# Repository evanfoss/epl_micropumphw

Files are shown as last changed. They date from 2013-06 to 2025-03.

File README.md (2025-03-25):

# EPL Micropump Hardware

This project was the hardware to be accompanied by the <a href="https://github.com/EPL-Engineering/epl_impup-fw">EPL Micropump Firmware</a> which is <a href="https://github.com/evanfoss/epl_micropumpfw">mirrored here</a>. The pair of projects is a wearable intracochlear drug delivery pump.

WARNING: This device is not for use on humans. It was experimental and not intended for actual medical use.

## History
1. The initial version was done by Ishmael S. Wagner it was built in a large inclosure from Bud Industries.
2. The 2nd version was built based on the original by Evan Foss & Ishmael S. Wagner. It fit in an enclosure 3D printed and covered in kapton tape by Draper Lab.
3. The 3rd version was a revision on the 2nd by Evan Foss & Ishmael S. Wagner. The board was produced but the project was canceled by the PI.

### Acknowledgements

I would like to thank Dianna Sands for the suggestion of using a balloon as the reservior.

## Specifications

* Small size
* Low weight
* Long battery life (+1 Week)
* Rechargable batteries
* Consisten flow rate and pressure over whole operating life
* Status indicator LEDs
* Pushbutton to prime fluid lines
* 2 Position switch to set operating mode (optional)
* Potentiometer to set flow rate (optional)

# Development

## Toolchain

The development toolchain was as follows:

|Tool Name                                                                                   | License           | Function
|:---------------                                                                            | :-------------    | :-----------------
|<a href="https://github.com/lepton-eda/lepton-eda">lepton-eda</a>                           | Open Source       | EDA (Electronic Design Automation) suite lepton-eda a fork of gEDA
|<a href="http://repo.hu/projects/pcb-rnd/">pcb-rnd</a>                                      | Open Source       | CAD (Computer Aided Design) tool for PCB (Printed Circuit Board) layout gEDA/PCB
|<a href="https://gerbv.github.io/">gerbv</a>                                                | Open Source       | Gerber viewer
|<a href="https://www.gnu.org/software/make/">GNU/Make</a>                                   | Open Source       | Toolchain automation

Note: The CAD drawings for the 3D printed case are lost to history is the name of the software used to draft them.

## Circuit Design

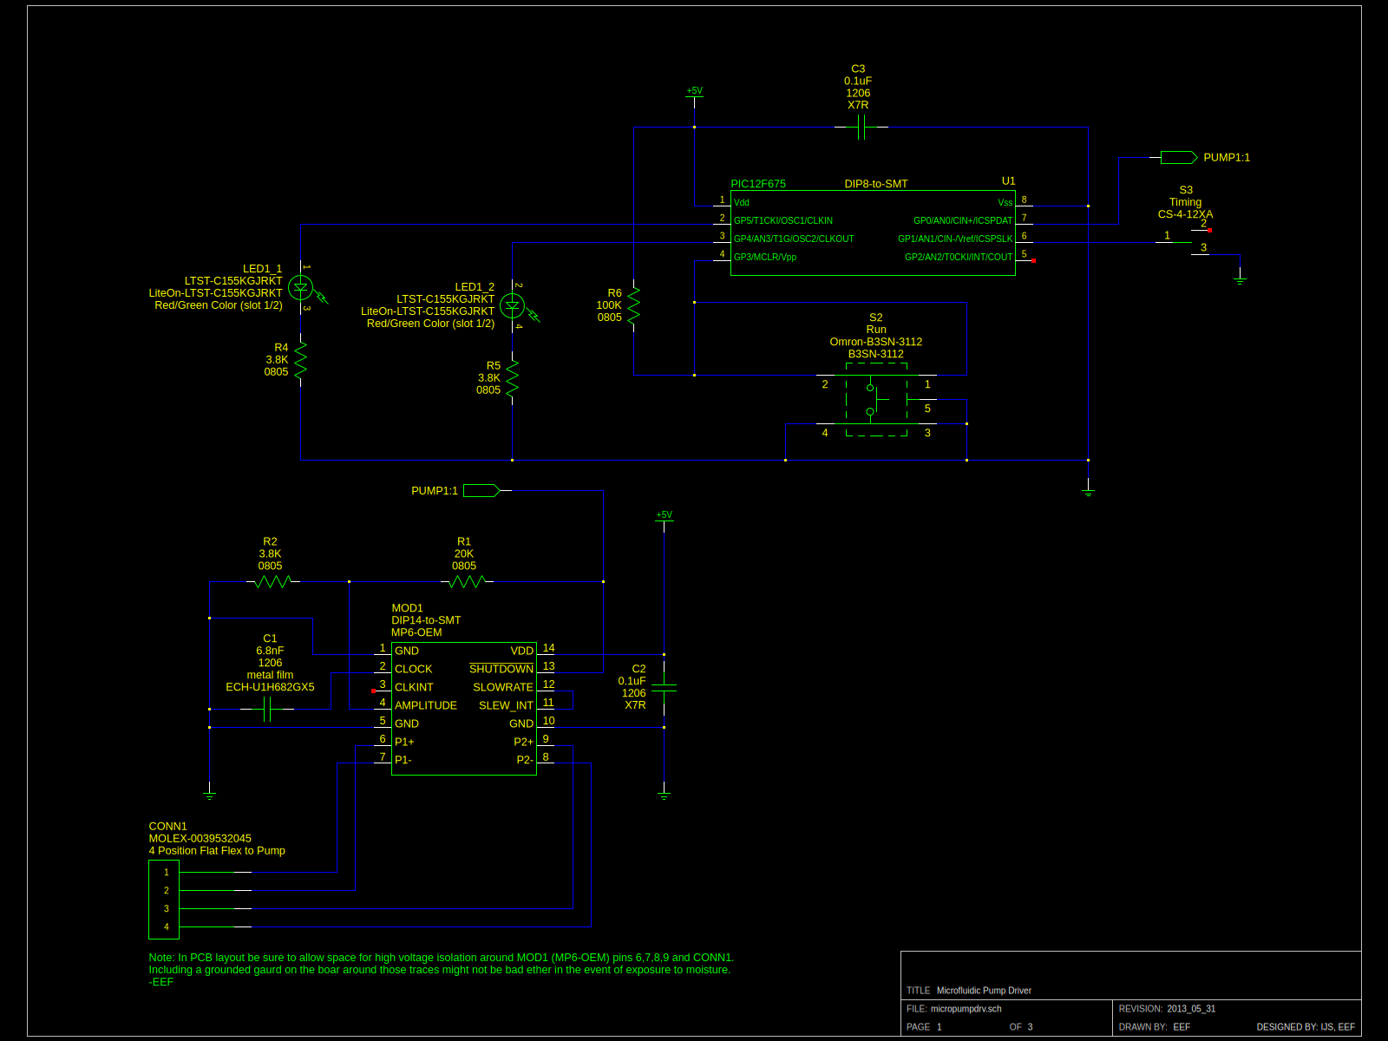
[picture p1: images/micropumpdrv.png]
|
|:---------------
|Sch1: micropumpdrv.sch

The device is based around the Bartels <a href="https://bartels-mikrotechnik.de/wp-content/uploads/2025/03/mp6-accessories-Catalogue-v1.11.pdf">microfluidic pump</a> that is piezo electric. The <a href="https://www.servoflo.com/images/PDF/mp6-oem-manual.pdf">pump driver</a> had an integrated DC/DC converter.

The wide operating voltage of the pump driver's DC/DC converter and the microcontroller's wide operating voltage the whole circuit can run off battery without any added voltage regulation.

The LED's and the pump are connected to output lines on the microcontroller. The switches are connected to inputs. Debounce of the switch is handled in firmware.

The pump driver module configuration is inspired by page 10 of the datasheet. Speed is set by the pulse train from the microcontroller output.

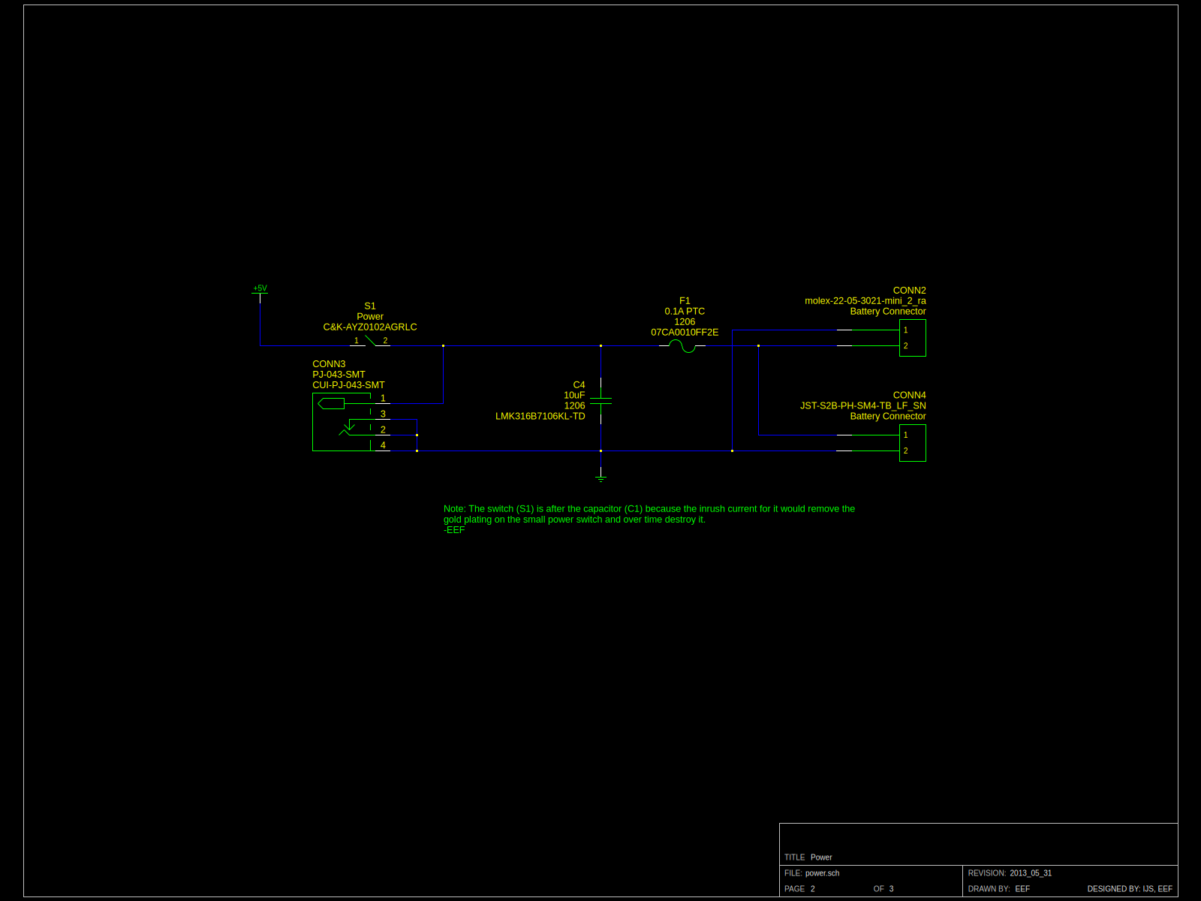
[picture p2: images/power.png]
|
|:---------------
|Sch2: power.sch

The power supply is just a fuse, on/off switch, and a fuse. There was some concern about a short triggering thermal runaway of the battery.

CONN2 and CONN4 were changed from the original single soldered wire in line connector for the last revision. That will be explained more later in Assembly.

CONN3 was added so that the PCBA and battery could be recharged as a single assembly because most of the breakdowns of the 1st wearable version were from misshandling. They were changing the battery far more frequently than they needed too. 

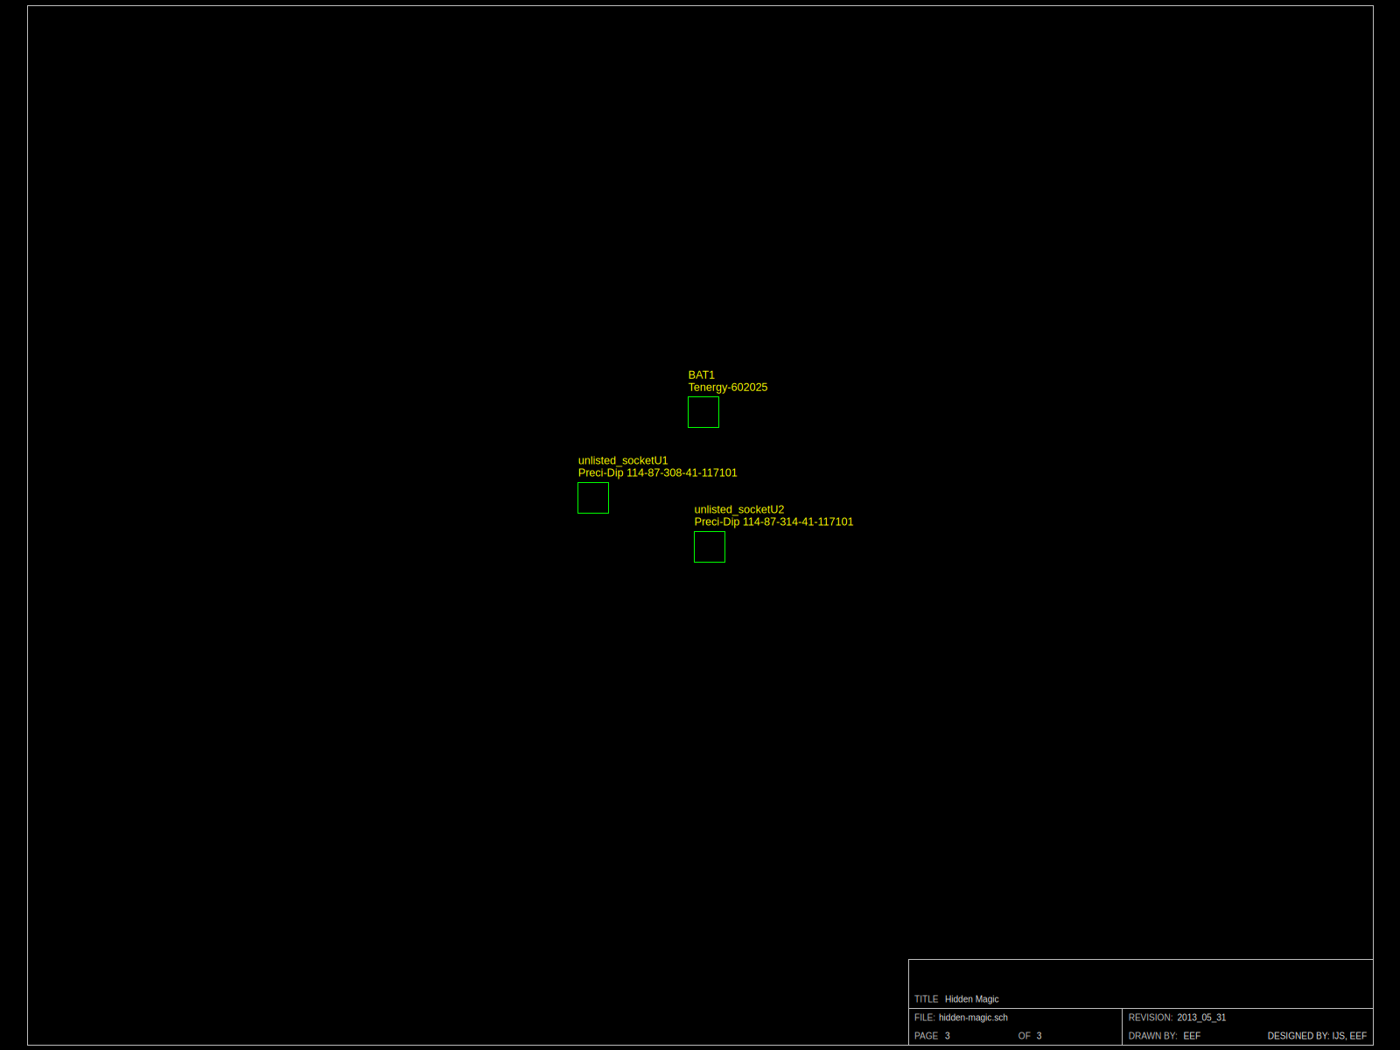
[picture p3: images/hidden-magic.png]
|
|:---------------
|Sch3: hidden.sch

The boxes in Sch3 is there to make the PCB software add boxes to help me track some mechanical keepouts etc that otherwise don't map to devices with pins.

## Printed Circuit Board Layout

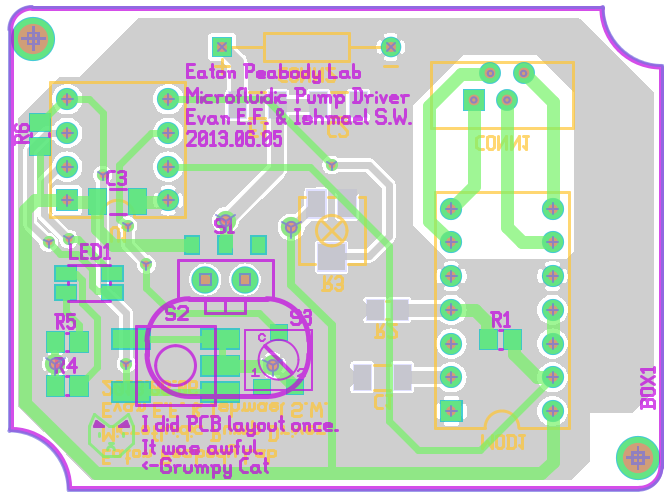
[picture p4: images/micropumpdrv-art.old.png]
|
|:---------------
|PCB1: Rendering of the 2nd version of the device. This was the first wearable version.

The 1st version of the layout shown in PCB1 had a bug that shorted the +V rail to ground but this was fixed later. As it was the board still technically worked but with a very short battery life (1day vs +1week).

|
|:---------------
|PCBA1: Top of the PCBA with the schematic for the micropumpdrv.sch sitting under it and a fine point sharpie for scale.

|
|:---------------
|PCBA2: Bottom of the PCBA with the same objects around it for scale

The PCB as shown required a little rework later. More on that later.

## Assembly

|
|:---------------
|ASSY1: The top cover with PCBA installed in it.

|
|:---------------
|ASSY2: The top and bottom of the device disassembled. The battery and pump in the bottom of the image.

This is the first working version.

I really didn't like the battery clip's protruding metal spring clip. That was meant to be changed in the next version.

## Future

Well there was the canceled version shown in PCBA2 meant to fit the bottom case in ASSY3.

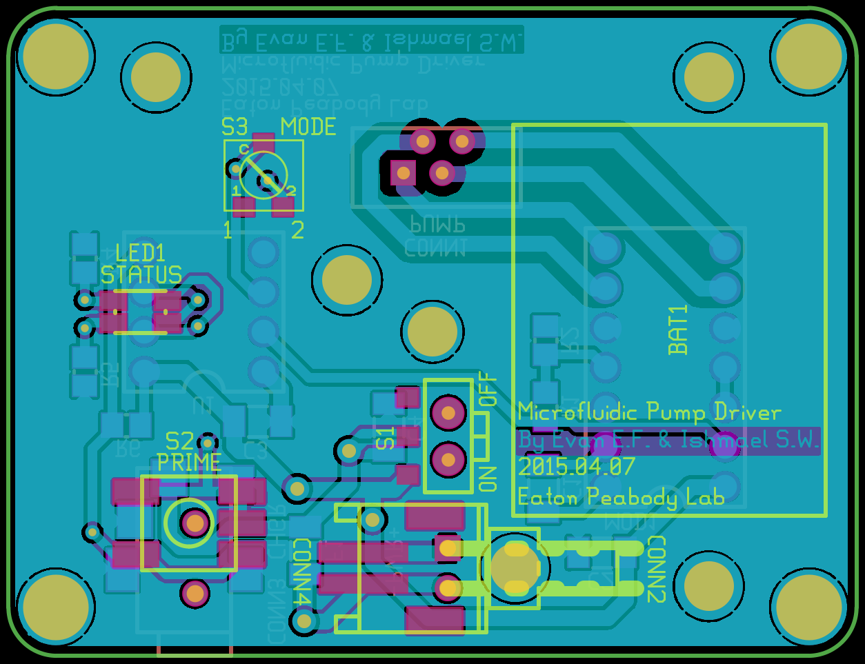
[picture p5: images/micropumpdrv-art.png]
|
|:---------------
|PCB2: Rendering of the 3rd version of the device.

PCB2 is the last designed version. The PCB was fabricated and an enclosure made but work stopped there. For those wondering about exposed connections unlike the prototype almost all sockets are surface mount. Exposed connections would probably have been covered with RTV-748 or a think cover would have been 3D printed too.

|
|:---------------
|ASSY3: Photo of the bottom of the case provided by the team over at Draper.

The denser layout of PCB2 was made possible by the DIP sockets that are SMT mounting. This makes using both sides of the PCB much simpler but it means the PCB basically must be hand populated.

The added holes in the PCB are for a few reasons. The center hole is for a thumb screw that was meant to go into the chassis where a threaded shaft was meant to hold the PCB down. The other holes were for winding the battery wires through the board for strain relief. The idea was to mount the battery to the PCB and just replace the whole PCB and battery assembly when recharging is required and to have the pump, tubing, and reservior mounted in the bottom of the chassis. The PCBA was intended to be the lid.

A more advanced pump capable of pumping in both directions instead of relying on back pressure to cause mixing would have been am improvement but Bartels didn't make a device like that at the time. 

A tuned cavity should be added to the fluidic circuit to reduce acoustic noise from the pump. Draper did a design after ours that never quite worked but it attempted to impliment the whole design in layers of kapton that were laser cut and welded. This was folly for a few reasons but the tuned cavity should be revisited.

At the time EPL didn't have the ability to do 3D CAD so if it was to happen again a redesign would not be using an outside company for the chassis.

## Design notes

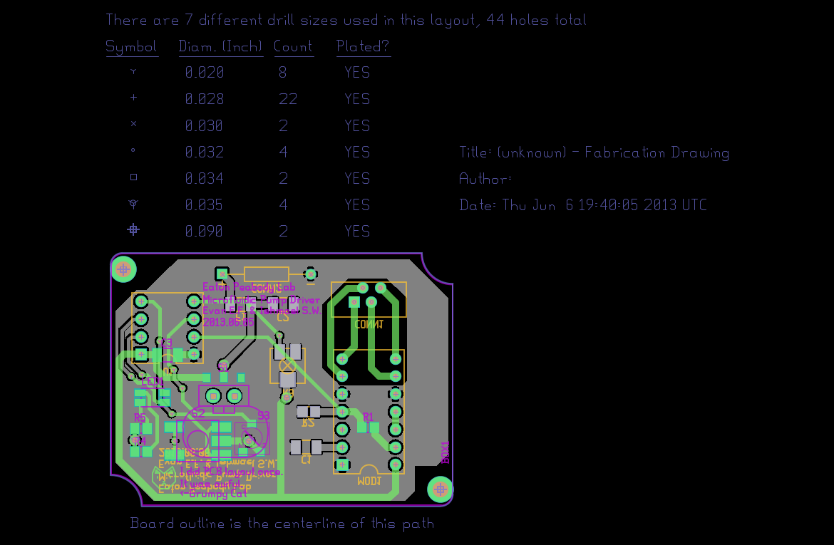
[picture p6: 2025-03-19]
images/photos/micropumpdrv-art_8971780404_o.png

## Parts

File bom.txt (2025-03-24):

Quantity	Part#			Manufacture		Catalog#			Distributor		RefDes.			Description
1		114-87-314-41-117101	Preci-Dip		114-87-314-41-117101-ND		Digikey			n.a.			14 Pin DIP Socket SMT for MOD1
1		114-87-308-41-117101	Preci-Dip		1212-1031-ND			Digikey			n.a.			8 Pin DIP Socket SMT for U1
1		PIC12F675-I/P		Microchip Tech.		PIC12F675-I/P-ND		Digikey			U1			8-Bit 20MHz 1.75KB (1K x 14) FLASH 8-PDIP
1		LTST-C155KGJRKT		Lite-On			160-1409-1-ND			Digikey			LED1			LED Red/Green Color, Red forward 2V typical, Green forward 2V typical
1		B3SN-3112		Omron Electronics	Z5200-ND			Digikey			S2			SPST Pushbutton Switch with grounded exterior, Waterproof
1		CS-4-12XA		Nidec Components	CS-4-12XA-ND			Digikey			S3			SPDT Rotary Switch, 100mA 16V Rated
1		AYZ0102AGRLC		C & K			401-2012-1-ND			Digikey			S1			Slide Switch SPDT Surface Mount, Right Angle
1		0039532045		Molex			WM2851-ND			Digikey			CONN1			4 Position FFC, FPC Connector Contacts, Vertical - 1 Sided 0.049" (1.25mm) Through Hole
1		PJ-043-SMT-TR		CUI (now Same Sky)	CP-043PJCT-ND			Digikey			CONN3			Power Barrel Connector Jack 1.10mm ID (0.043"), 3.00mm OD (0.118") Surface Mount, Right Angle
1		0022053021		Molex			900-0022053021-ND		Digikey			CONN2			Connector Header Through Hole, Right Angle 2 position 0.100" (2.54mm)
1		S2B-PH-SM4-TB		JST			455-S2B-PH-SM4-TBCT-ND		Digikey			CONN4			Connector Header Surface Mount, Right Angle 2 position 0.079" (2.00mm)
1		LMK316B7106KL-TD	Taiyo Yuden		587-2596-1-ND			Digikey			C4			10 µF ±10% 10V Ceramic Capacitor X7R 1206
1		07CA0010FF2E		Bell Fuse (probably)	??				??			F1			0.100A PTC Fuse, no longer manufactured or distributed
1		ECH-U1H682GX5		Panasonic		PCF1306CT-ND			Digikey			C1			6800 pF Film Capacitor 30V 50V Polyphenylene Sulfide (PPS), Metallized - Stacked 1206
1		MP6-OEM			Bartels			-				-			MOD1			Bartels Pump Driver Module 14 Pin DIP Package
1		602025			Tenergy			-				-			BAT1			3.7V 250mAH Lithium Ion Small Model Aircraft Battery
2		C1206C104K5RACTU	KEMET			399-C1206C104K5RACTUCT-ND	Digikey			C2, C3			0.1 µF ±10% 50V Ceramic Capacitor X7R 1206 (generic part)
2		RWB3K800AL		VPG Foil Resistors	804-RWB3K800ALCT-ND		Digikey			R2, R4, R5		3.8 kOhms ±0.05% 0.2W, 1/5W Chip Resistor 0805 Metal Foil
1		RC0805FR-07100KL	YAGEO			311-100KCRCT-ND			Digikey			R6			100 kOhms ±1% 0.125W, 1/8W Chip Resistor 0805 (generic part)
1		RC0805FR-1320KL		YAGEO			13-RC0805FR-1320KLCT-ND		Digikey			R1			20 kOhms ±1% 0.125W, 1/8W Chip Resistor 0805
1		MP6			Bartels			-				-			-			Bartels Piezo Electric Pump

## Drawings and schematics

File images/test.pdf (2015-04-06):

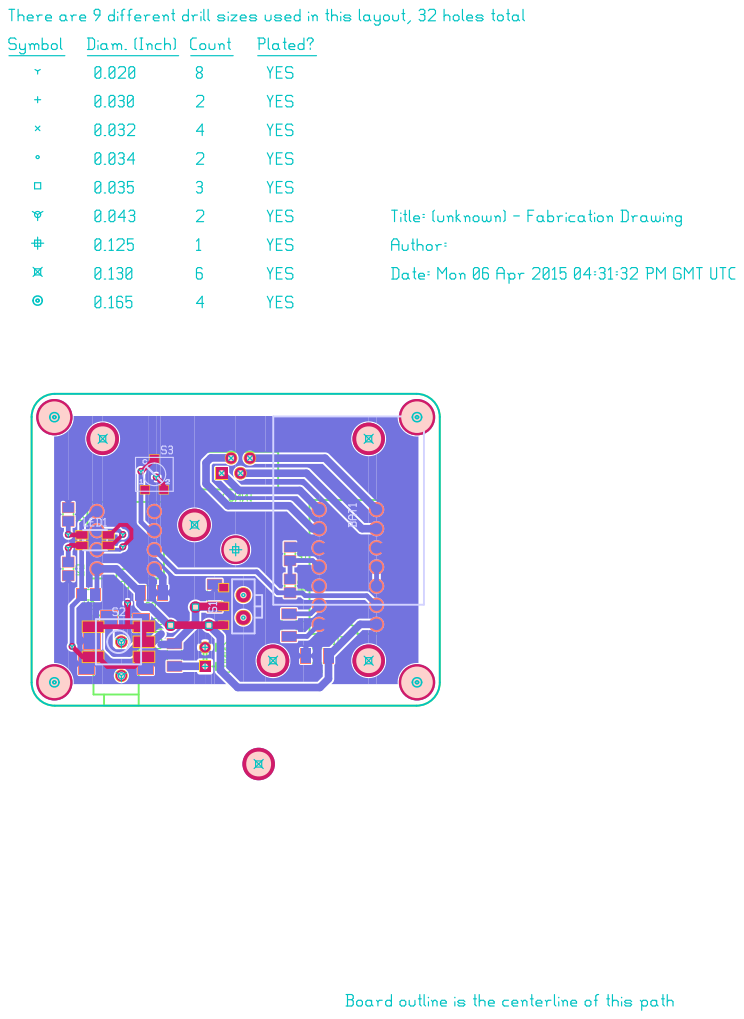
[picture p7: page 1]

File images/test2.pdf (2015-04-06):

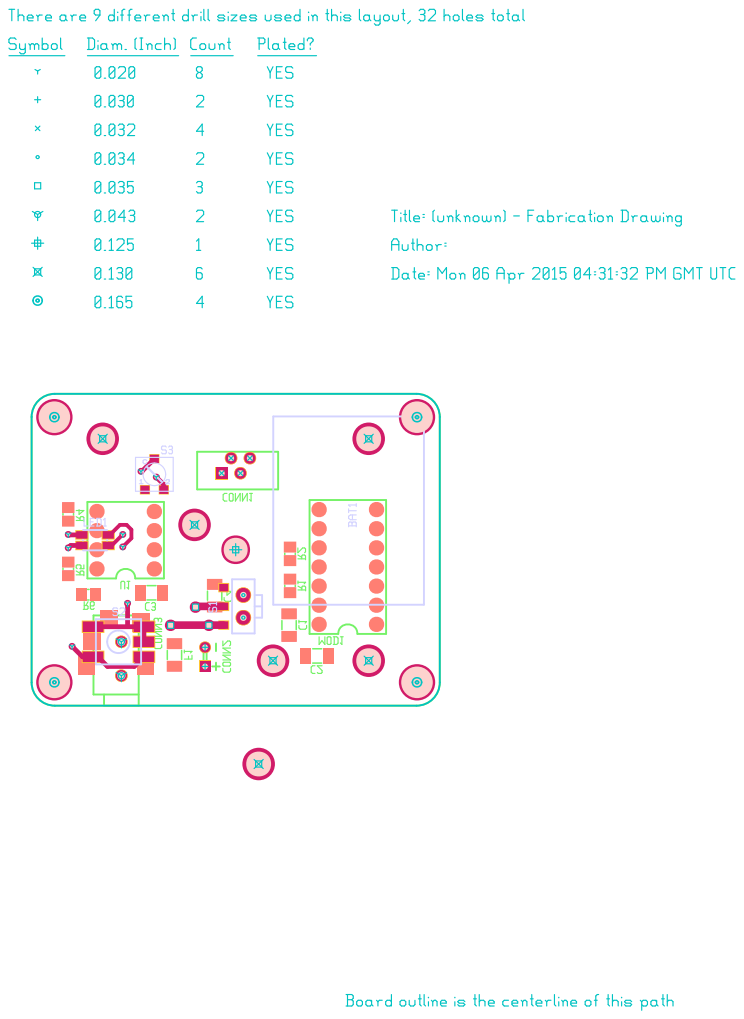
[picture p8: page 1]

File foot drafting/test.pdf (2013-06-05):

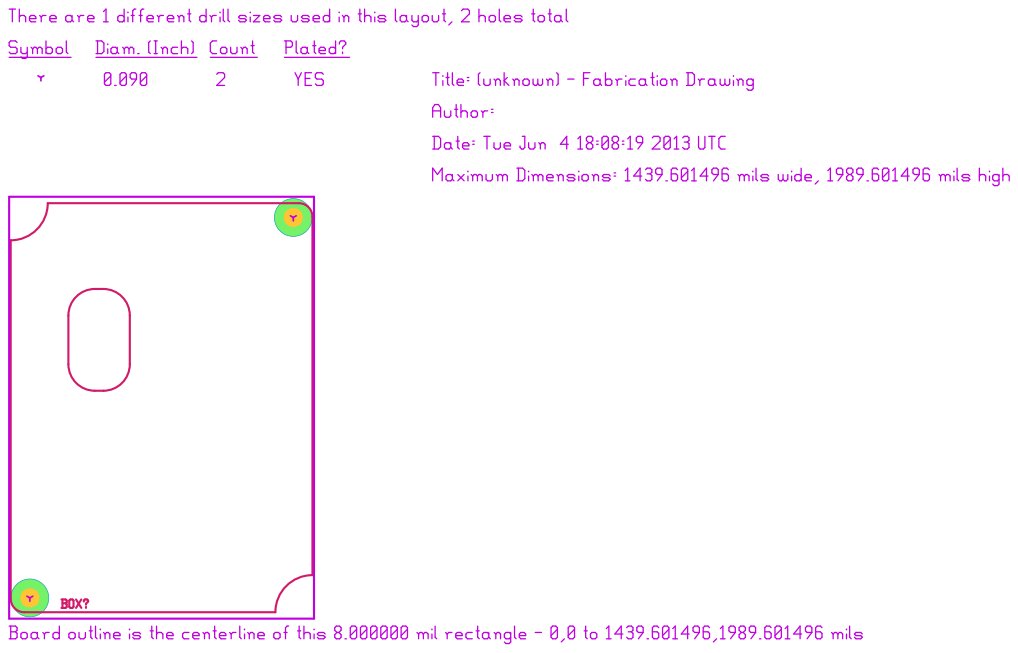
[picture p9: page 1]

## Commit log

2013-05-30 Initial commit-schematic entered pcb layout in progress
    [hidden-magic.sch, micropumpdrv.sch, power.sch]
2013-05-31 I still need to add holes for board mounting and i realized the layout is flipped.
    [hidden-magic.sch, micropumpdrv-art.bottom.gbr, micropumpdrv-art.bottommask.gbr, micropumpdrv-art.bottompaste.gbr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]
2013-05-31 everything *should* line up now
    [micropumpdrv-art.bottom.gbr, micropumpdrv-art.bottommask.gbr, micropumpdrv-art.bottompaste.gbr, micropumpdrv-art.bottomsilk.gbr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]
2013-06-05 I mostly fixed the board alignment issue the mechanical documentation does not match the product
    [micropumpdrv-art.bottom.gbr, micropumpdrv-art.bottommask.gbr, micropumpdrv-art.bottompaste.gbr, micropumpdrv-art.bottomsilk.gbr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]
2013-06-06 Added images of schematics and layout, added board outline and improved silk screen
    [hidden-magic.sch, micropumpdrv-art.bottom.gbr, micropumpdrv-art.bottommask.gbr, micropumpdrv-art.bottompaste.gbr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]
2013-07-19 fixed B3SN-3112 symbol, fixed TS53YL104MR10 symbol, corrected board
    [micropumpdrv-art.bottom.gbr, micropumpdrv-art.bottommask.gbr, micropumpdrv-art.bottompaste.gbr, micropumpdrv-art.bottomsilk.gbr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]
2015-02-03 adjusting title blocks and exported imagery for the ARO poster.
    [hidden-magic.sch, micropumpdrv-art.bottom.gbr, micropumpdrv-art.bottommask.gbr, micropumpdrv-art.bottompaste.gbr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]
2015-04-02 fixed issue with C4, changed layout for version 2, moving to accomodate center post and in circuit charging.
    [hidden-magic.sch, micropumpdrv.sch, power.sch]
2015-04-06 revised outline, battery on top, added holes for mounting cover to pcb and etc
    [hidden-magic.sch, micropumpdrv-art.bottom.gbr, micropumpdrv-art.bottommask.gbr, micropumpdrv-art.bottompaste.gbr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]
2015-04-08 2nd version shipped
    [hidden-magic.sch, micropumpdrv-art.bottom.gbr, micropumpdrv-art.bottommask.gbr, micropumpdrv-art.bottompaste.gbr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]
2015-04-10 bom for version 2 is being improved
    [power.sch]
2025-03-19 add: pictures of the assembled device in prototype
2025-03-22 cleaup: removed old junk and reorganized
    [micropumpdrv-art.bottom.gbr, micropumpdrv-art.bottommask.gbr, micropumpdrv-art.bottompaste.gbr, micropumpdrv-art.bottomsilk.gbr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]
2025-03-22 del: removed the packaged ordering info for alberta printed circuits
    [micropumpdrv-art.bottom.gbr, micropumpdrv-art.bottommask.gbr, micropumpdrv-art.bottompaste.gbr, micropumpdrv-art.bottomsilk.gbr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]
2025-03-22 add: pcb images
2025-03-22 add: images of the assembled device
2025-03-24 add: more pictures of the assembled device.
2025-03-24 add: images of case
2025-03-24 add: cropped image of bottom case
2025-03-25 add: migrated to lepton-eda and pcb-rnd
2025-03-25 add: readme more on pcb as cover
2025-03-25 add: more notes on pcb connectors
